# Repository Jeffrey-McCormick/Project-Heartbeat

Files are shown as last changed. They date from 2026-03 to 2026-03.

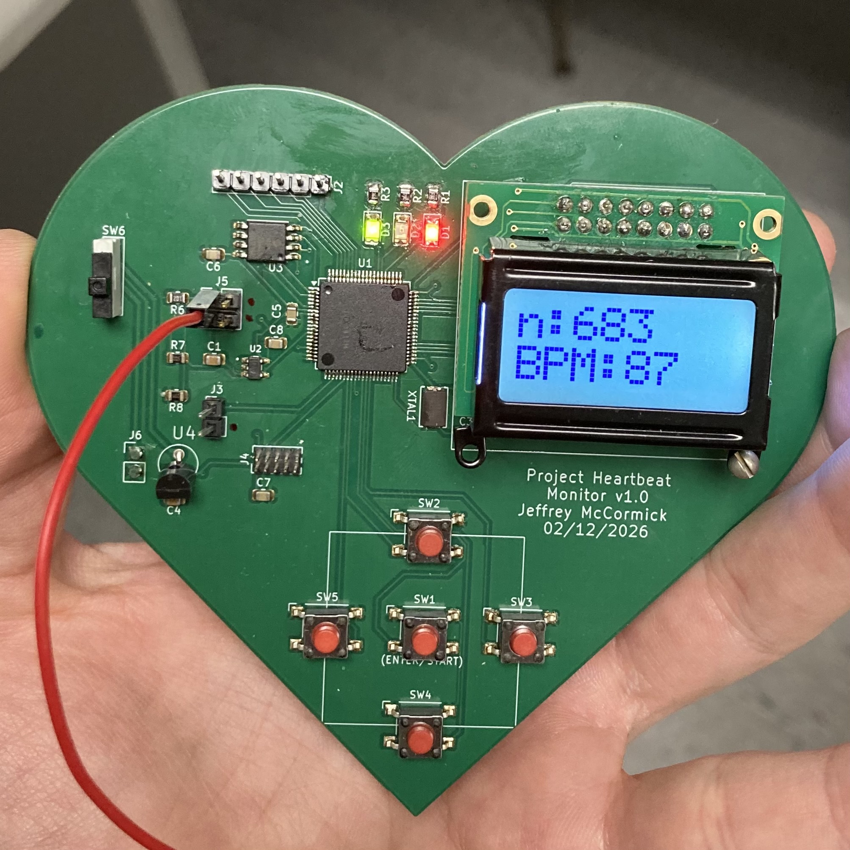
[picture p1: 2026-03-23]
IMG_8756.jpeg

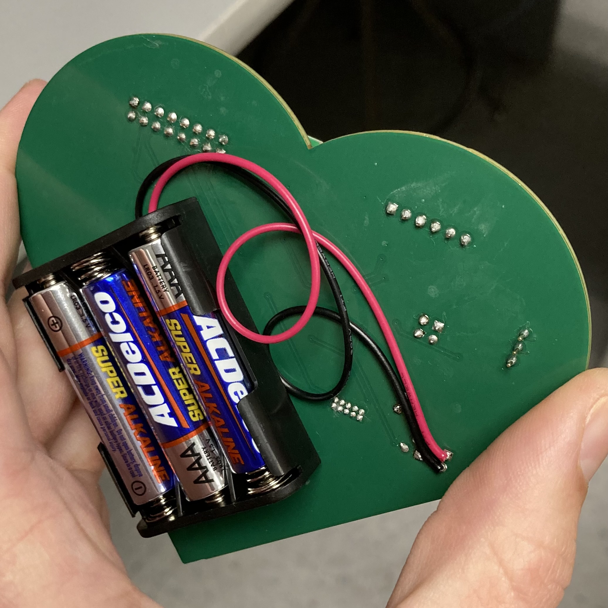
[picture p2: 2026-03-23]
IMG_8758.jpeg

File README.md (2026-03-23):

Hello! Welcome to Project Heartbeat, my individual project for my ENGR 355 - Embedded System Design class.
This project's first revision is finished and turned in for credit. Later versions may appear as I have opportunity to expand this heartrate monitor's capabilities. I used KiCad and ARM Keil applications for designing and programming the board. 

I encourage you to read the Project Heartbeat Design Report to understand my design approach as well as what the functions of my code are for. 
Although, you should be able to read the comments in my code and understand what is happening. 

Here is what it looked like in KiCad and in reality.




The text I used was produced by ARM Education. Here is the Github resource: https://github.com/arm-education/Embedded-Systems-Fundamentals?tab=readme-ov-file

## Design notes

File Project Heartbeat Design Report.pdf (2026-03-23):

# Project Heartbeat’s Embedded System Design

Jeffrey A. McCormick, Student, Walla Walla University

Abstract— This project seeks to use an analog to digital converter (ADC) to determine the heartrate of a person from an analog electrocardiogram (EKG) waveform.

I. INTRODUCTION
IGNAL processing is at the foundation of many breakthrough technologies. From car radios to medical scanning systems, most of all sensor equipment is used to measure continuous “real-world analog signals”. [3] By using an ADC, those analog signals can then be processed digitally on, say, a computer or calculator or an FPGA.
For the embedded system called Project Heartbeat, an ADC will be used to convert an analog heartbeat signal and use the digital representation of it to compute and display for the user an extrapolated beats per minute (BPM) measure.

II. DESIGN METHODS: HARDWARE
The general approach to designing the hardware for Project Heartbeat relied heavily on the KL25Z FRDM board,ENGR 355 Dev board, and LCD specifications. Since their designs worked well together, making a custom Printed Circuit Board (PCB) that would seamlessly integrate into this system was paramount. A distinct benefit of using this approach was that I could program and test using the Dev board, while the parts and custom PCB were being delivered.
While the Dev board schematic was the pattern, there were several changes of note. First, the system had to be portable, meaning that the Project Heartbeat device would have to be battery powered. To accommodate this, a physical on-off switch and a voltage regulator were added to the schematic. The supplied voltage from the regulator was 3.3V to be used as power for the rest of the system.
Second, | in | order | to | program | the | MKL25Z128
microcontroller (MCU), a 10-pin header Serial Wire Debug (SWD) interface was added. The FRDM board would connect to this interface but only use six of the ten pins. Per the FRDM KL25Z Schematic indicating that the SWD clock and digital input/output pins should go on Port A pins 0 and 3, respectively, some of the switches were displaced to other pins.
Third, the five switches were still connected to Port A of the MCU so that they could have interrupt capabilities, but they were rearranged. The layout of the PCB was to have the five buttons arranged like a Swiss cross with SW1 centered and the others ordered sequentially clockwise around it. By this schematic arrangement, their traces on the PCB were more organized, taking up less space and reducing the risk of layout

mistakes.
Fourth, six GPIO pins were placed on Port D, because that gives the designer maximum future project flexibility in case they wish to use interrupts with such pins.
Fifth, an EEPROM memory chip was added. Again, this was chosen with future projects by the designer in mind, providing a way for users to read and write data for long-term storage without burdening the microcontroller’s memory. Sixth, the ADC input was designed for both DC and AC coupling. The AC coupling input passes through a voltage divider such that a signal of 0V AC enters the buffering source follower op amp, delivering an input of 1.65 V into the ADC. DC inputs are simply buffered without the scale shift.
As good practice, coupling capacitors were placed near the power pins of the MCU, SWD interface, LCD interface, ADC source follower op amp, and EEPROM. These were chosen to dampen any voltage fluctuations in the 3.3V power and to reduce the risk of noise adding to the signals.
The PCB layout was designed for an easy and intuitive user experience as well as convenient debugging and flexible application. Many people in this modern digital era are familiar with Gameboy or other handheld Nintendo products, so the Project Heartbeat board layout was modeled after them. The hope is that a user can figure out how to use the board by drawing on this familiarity of an LCD screen with buttons below it. Since the primary use case of the board was to detect and calculate heartbeat behavior, it seemed fitting to let the user’s intuition know that by making the board heart shaped. Although it may still be encased within a plastic covering, the board could still be used pleasantly without the covering by designers, developers, and debuggers. Therefore, the size of the board was made approximately 4 inches by 3 inches to fit comfortably in an average person’s hand(s), even though a more compact layout could have had the same electronic functionality. With a less compact layout, the board’s components can be easily accessed by a developer trying to debug the circuitry.

S

IMAGE 1
THIS IS THE FRONT VIEW

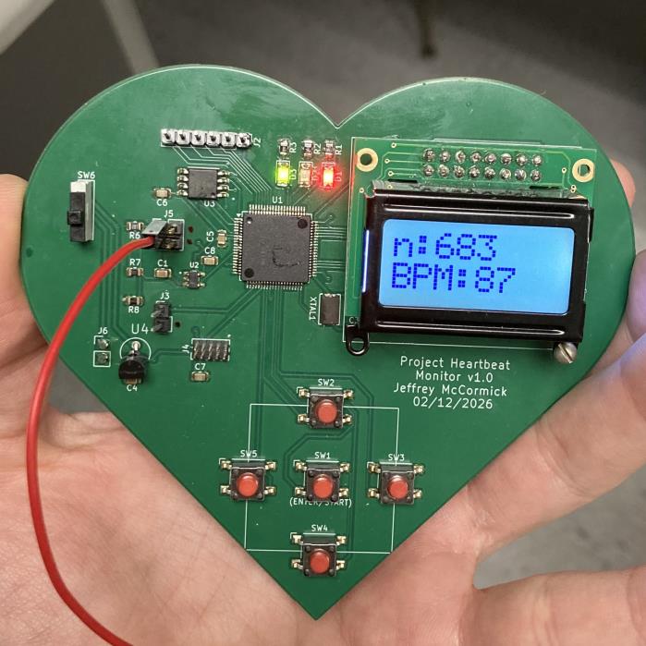
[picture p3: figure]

McCor1.jpeg

IMAGE 1
THIS IS THE BACK VIEW

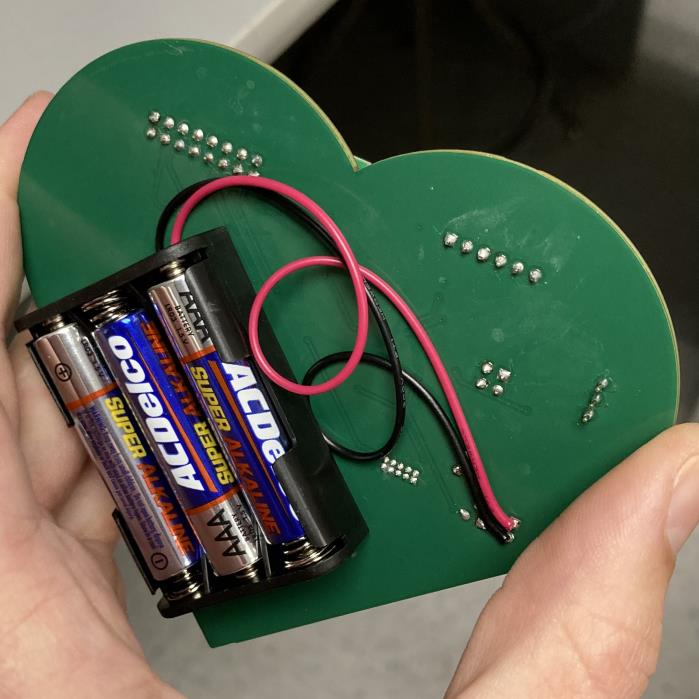
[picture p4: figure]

McCor2.jpeg

IV. DESIGN METHODS: SOFTWARE The software of Project Heartbeat was made for the primary use case of receiving a continuous analog heartbeat signal and output the BPM corresponding to the interval between the last two beats sensed. To make debugging easier, a modular approach was taken. The “main” function served as the testbench code for each function as they were being developed. This strategy ensured that any errors in the inputs and outputs of a function were caught early and corrected. Artificial intelligence (AI) was used as a tool to expedite each function’s code generation by prompting with specific desired inputs, outputs, purpose, and role in the software and project as a whole. Because the software functions are not placed in order of their dependency in the “Lab_8_Code.c” c-language code file, the following explanations of the code will be presented in order of their dependency from input to output.

A. Enable the Clocks
This ENABLE_CLKS() function enables the default system clock signal in Clock Setup 1 (48MHz) to go to Ports A, B, C, and E of the MCU. It is mostly just to ensure the code is completely enabled or disabled by whether the function is called or not, respectively.
B. Initialize ADC
The Init_ADC() function sets the ADC to:
1) 12-bit conversion standard
2) Clock division by 4
3) Clock source of ADICLK (default)
It also enables the ADC0 conversion complete flag (COCO) to trigger an interrupt to be handled in the ADC IRQ Handler.
C. Initialize SysTick Interrupts
For use in other functions as an independent timer from the PIT, this Init_SysTick() function simply sets the ticks to occur once every 1ms and trigger an interrupt with it.
D. Initialize PIT and Define Its IRQ Handler
Similar to the SysTick initialization, the PIT_init() function serves to enable interrupts which occur exactly once per 1ms. It’s PIT_IRQHandler() function can then increment the two counters used by the buttons for debouncing and the heartbeat interval calculator for measurement. A green LED is linked to every PIT flag raising so that the user can know if the device is on and running.
E. Initialize Buttons and Define Their Port A ISR Handler Init_Buttons() sets all the buttons to input GPIOs with pull-up resistor setting configured in the MCU and with interrupt capabilities. Then, because the buttons are on Port A, the PORTA_IRQHandler() function triggers when a button is pressed and uses the system millisecond counts from the PIT to debounce the button press and set a program flag as true.

F. Initialize the DAC
This Init_DAC() function simply sets the DAC as active and referencing the same reference voltage as the other components.
G. Define ADC IRQ Handler
This ADC0_IRQHandler() function operates in two modes. Mode 1 is the most useful mode, because it sets the DAC to be an output for reconstruction of the input heartbeat signal. Mode 2 sets the DAC as a simulator essentially so it does not need to be tied to the ADC’s output.
The function triggers whenever the input converted signal crosses the threshold and hysteresis digital voltage values. They can be set to DC and AC coupling, which only changes whether the interrupt is triggered on the rising or falling edge of a beat. See code comments for examples.
A red LED is used as an indicator that a conversion happened.
H. Get the Heartbeat from the ADC Signal
When a conversion completes, this get_heartbeat() function simply captures the current PIT count in the interval between beats and resets the count to be ready for the next beat. The PIT increments every 1ms, so the PIT counts that happened in the interval is equivalent to the number of milliseconds between the beats.
I. Initialize LEDs
This Init_LEDs() function simply sets the LEDs to GPIO outputs so that they can be used as indicator lights.
J. Get BPM from the Heartbeat Intervals in Milliseconds This get_bpm() function is the convert the beat interval in ms found by the get_heartbeat() function into the calculated BPM corresponding to a period equal to the length of that interval. While this lends itself to greater fluctuation in the calculated BPM for small deviations from an average input signal’s BPM, it allows for processing as close to present as possible so that a “live” data stream can be viewed by the user. The calculation uses integer math to save computation time and memory space of the MCU. Again, the goal is as close to a real-time update as possible.
K. Initialize LCD and Display a String of Relevant Data Using the unaltered “lcd_lib_4bit_20b.c” LCD library of commands file written by Dr. Larry Aamodt, the LCD_init() function initializes the LCD. Displaying a string on any selectable line of the LCD is the purpose of the displayString() function. By supplying a character array to display and the line selection of 0 for the top line and 1 for the bottom line, the LCD will display only the first 8 characters in the string on the selected line. This function allows explicit developer control over what is shown on the LCD screen.
L. The Main Function
The main function calls all of the above functions as needed for scope or simulator modes of the device. Within a while loop running faster than the 1ms PIT or SysTick interrupts, get_heartbeat() checks for a beat from the ADC, a simple LCD user interface tells users what the state of the program is, and running logic critical for “live” updates of the LCD ensures that recently captured and processed signal data is displayed on the LCD without race conditions. With the large amount of interrupts and the random nature of when a signal could enter the ADC, it is important that the transmission to the LCD finish before seeking another one. This could potentially cause under counting, but not if the signal period is greater than 2ms, which is true for heartbeat signals even up into the arithmetic heart rates (500+ BPM). Another timing aspect of the running logic is that the LCD should only update the display when the measured period between the beats actually changes. This task reduction results in more stable display behavior.
V. RESULTS

A demonstration of the Project Heartbeat board working as a live heartrate monitor in action was performed on March 17, 2026 on Jeffrey McCormick. Medical-grade EKG pads were placed at each shoulder and his left leg. The leads connected to an isolated amplifier circuit board made by Dr. Larry Aamodt, which then sent the signal ranging from 0v to 3.3V to the ADC input pins on the Project Heartbeat board.
The initial result was very high BPM measurements. To see what thresholds to adjust the code to, an oscilloscope was connected to the Project Heartbeat ADC pins. After increasing the threshold, the board read the live heartbeat signals within 5 percent error of the value from a standard Oura Ring 4
simultaneously | measuring | the | live | heart | rate | from
McCormick’s index finger.

VI. CONCLUSION

Overall, Project Heartbeat as a physical, custom embedded system met its essential requirements as specified by instructor Dr. Natalie Smith-Gray. It is “a hand-held portable instrument that can analyze a periodic analog input signal (voltage)[1] While its embedded system demonstrates promise, it can still be improved by adding a filtering or stream-averaging scheme to the software, more functions like HRV measurements, and a visually and physically appealing plastic case to hold it.

REFERENCES

[2] N. Smith-Gray, “ENGR 355 Course Project,”unpublished. Winter 2026. https://class.wallawalla.edu/d2l/le/lessons/379831/topics/4176668
[3] Nintendo Co. Game Boy. https://nintendo.fandom.com/wiki/Game_Boy (Accessed 18 Mar 2026)
[4] IC Online, “ADC vs DAC Key Differences and Modern Electronics
Applications,” | https://ic-online.com/blog/post/adc-vs-dac-key-
differences-and-modern-electronics-applications(Accessed 18 Mar 2026)

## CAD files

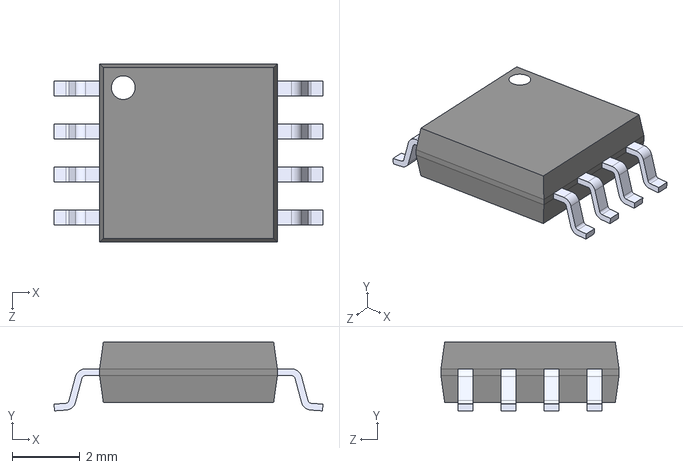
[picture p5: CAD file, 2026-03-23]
Project Heartbeat KiCad/P_4.1_2026_Jeff_M/25LC1024_I_SM/25LC1024-I_SM.step
7.94 x 2.03 x 5.26 mm

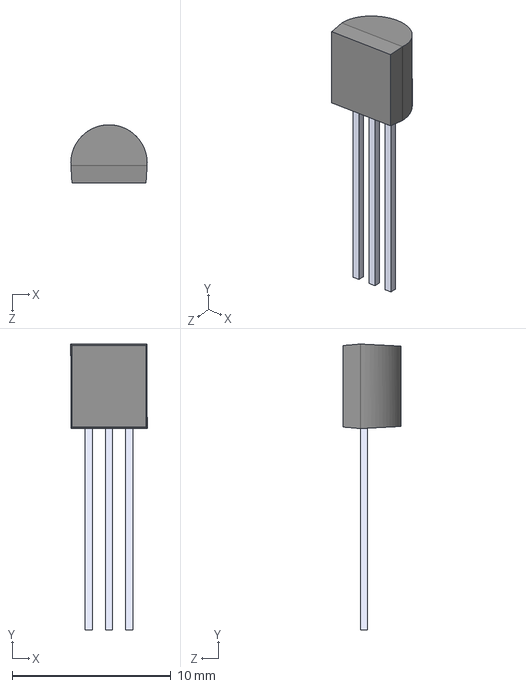
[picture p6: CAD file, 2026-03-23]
Project Heartbeat KiCad/P_4.1_2026_Jeff_M/MCP1700_3302E_TO/MCP1700-3302E_TO.step
4.82 x 18.0 x 3.68 mm

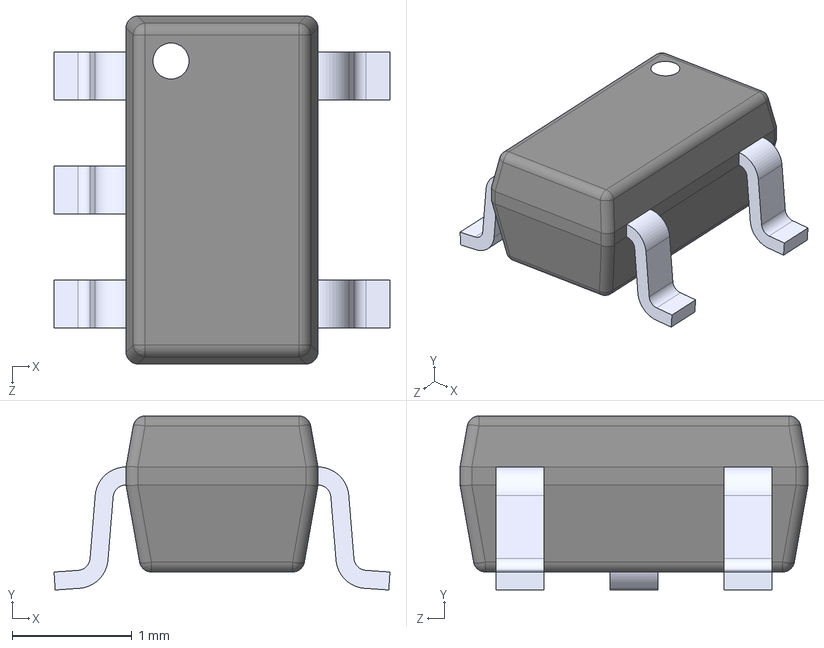
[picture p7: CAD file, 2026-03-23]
Project Heartbeat KiCad/P_4.1_2026_Jeff_M/OPA377AIDBVR/OPA377AIDBVR.step
2.80 x 1.45 x 2.90 mm

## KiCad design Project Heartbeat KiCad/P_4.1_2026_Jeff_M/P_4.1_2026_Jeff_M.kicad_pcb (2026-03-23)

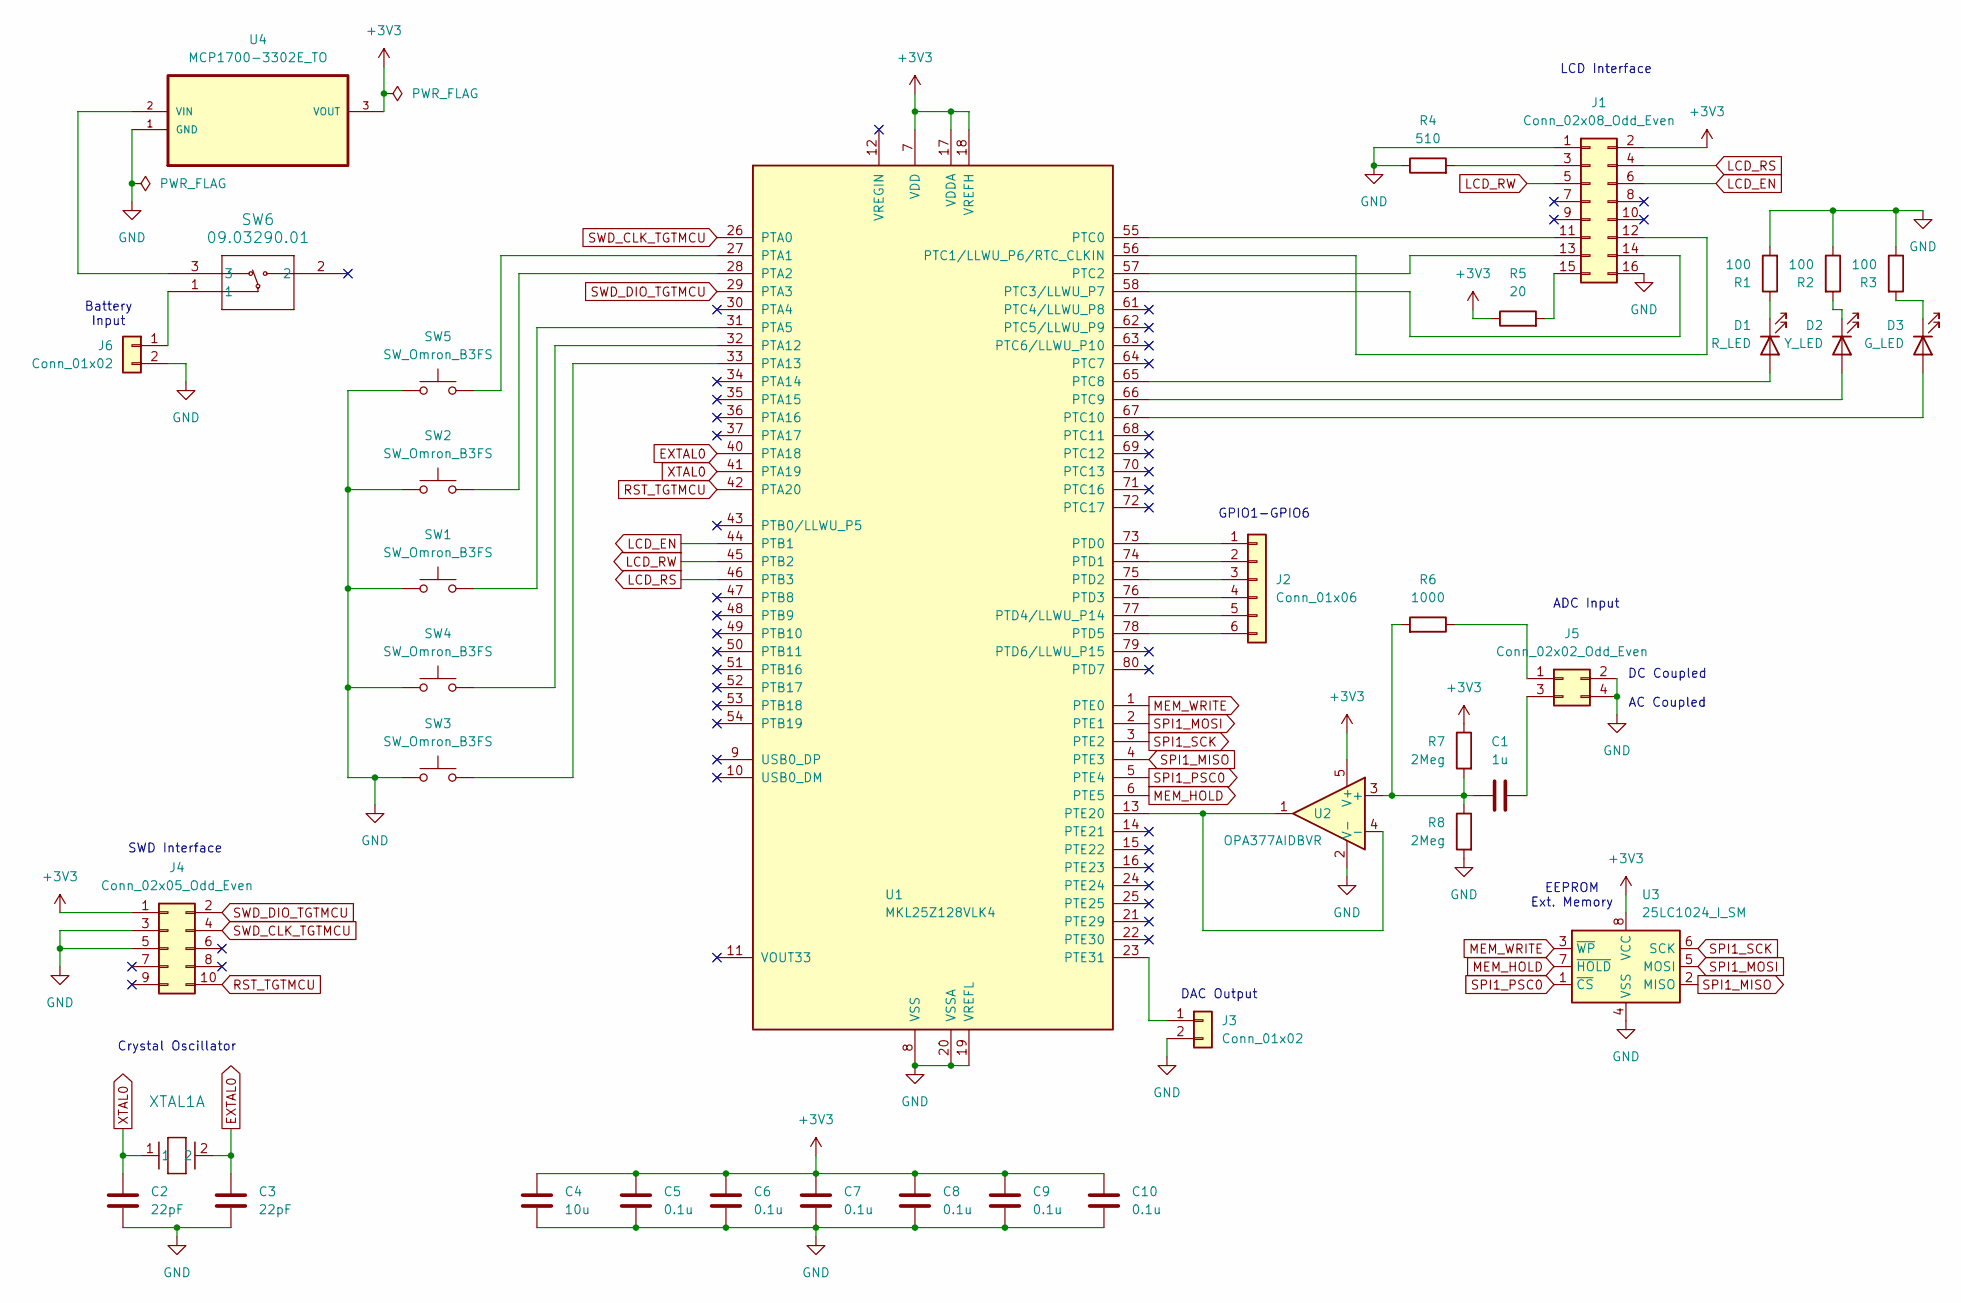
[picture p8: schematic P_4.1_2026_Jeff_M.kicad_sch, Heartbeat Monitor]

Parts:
C1: 1u; C_0805_2012Metric
C2, C3: 22pF; C_0805_2012Metric
C4: 10u; C_0805_2012Metric
C5, C6, C7, C8, C9, C10: 0.1u; C_0805_2012Metric
D1: R_LED; LED_1206_3216Metric
D2: Y_LED; LED_1206_3216Metric
D3: G_LED; LED_1206_3216Metric
J1: Conn_02x08_Odd_Even; PinHeader_2x08_P2.54mm_Vertical
J2: Conn_01x06; PinHeader_1x06_P2.54mm_Vertical
J3, J6: Conn_01x02; PinHeader_1x02_P2.54mm_Vertical
J4: Conn_02x05_Odd_Even; PinHeader_2x05_P1.27mm_Vertical
J5: Conn_02x02_Odd_Even; PinHeader_2x02_P2.54mm_Vertical
R1, R2, R3: 100; R_0805_2012Metric
R4: 510; R_0805_2012Metric
R5: 20; R_0805_2012Metric
R6: 1000; R_0805_2012Metric
R7, R8: 2Meg; R_0805_2012Metric
SW1, SW2, SW3, SW4, SW5: SW_Omron_B3FS; SW_SPST_Omron_B3FS-101xP
SW6: 09.03290.01; 09.03290_EAO
U1: MKL25Z128VLK4; LQFP-80_12x12mm_P0.5mm
U2: OPA377AIDBVR; SOT95P280X145-5N
U3: 25LC1024_I_SM; SOIC127P794X202-8N
U4: MCP1700-3302E_TO; TO127P254X495-3; MPN MCP1700-3302E/TO
XTAL1: ABM3-8.000MHZ-D2Y-T; XTAL_ABM3-8.000MHZ-D2Y-T_ABR

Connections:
+3V3: C4.1, C5.1, C6.1, C7.1, C8.1, C9.1, C10.1, J1.2, J4.1, R5.1, R7.1, U1.7 (VDD), U1.17 (VDDA), U1.18 (VREFH), U1.38 (VDD), U1.60 (VDD), U2.5 (V+), U3.8 (VCC), U4.3 (VOUT)
EXTAL0: C3.1, U1.40 (PTA18), XTAL1.2
GND: C2.2, C3.2, C4.2, C5.2, C6.2, C7.2, C8.2, C9.2, C10.2, J1.1, J1.16, J3.2, J4.3, J4.5, J5.2, J5.4, J6.2, R1.2, R2.1, R3.1, R4.1, R8.2, SW1.1, SW2.1, SW3.1, SW4.1, SW5.1, U1.8 (VSS), U1.19 (VREFL), U1.20 (VSSA), U1.39 (VSS), U1.59 (VSS), U2.2 (V-), U3.4 (VSS), U4.1 (GND)
LCD_EN: J1.6, U1.44 (PTB1)
LCD_RS: J1.4, U1.46 (PTB3)
LCD_RW: J1.5, U1.45 (PTB2)
MEM_HOLD: U1.6 (PTE5), U3.7 (~HOLD)
MEM_WRITE: U1.1 (PTE0), U3.3 (~WP)
unnamed: D1.2 (A), U1.65 (PTC8)
unnamed: D1.1 (K), R1.1
unnamed: D2.2 (A), U1.66 (PTC9)
unnamed: D2.1 (K), R2.2
unnamed: D3.2 (A), U1.67 (PTC10)
unnamed: D3.1 (K), R3.2
unnamed: J1.3, R4.2
unnamed: J1.11, U1.55 (PTC0)
unnamed: J1.12, U1.56 (PTC1/LLWU_P6/RTC_CLKIN)
unnamed: J1.13, U1.57 (PTC2)
unnamed: J1.14, U1.58 (PTC3/LLWU_P7)
unnamed: J1.15, R5.2
unnamed: J2.1, U1.73 (PTD0)
unnamed: J2.2, U1.74 (PTD1)
unnamed: J2.3, U1.75 (PTD2)
unnamed: J2.4, U1.76 (PTD3)
unnamed: J2.5, U1.77 (PTD4/LLWU_P14)
unnamed: J2.6, U1.78 (PTD5)
unnamed: J3.1, U1.23 (PTE31)
unnamed: J5.1, R6.1
unnamed: C1.1, J5.3
unnamed: J6.1, SW6.1
unnamed: SW5.2, U1.27 (PTA1)
unnamed: SW2.2, U1.28 (PTA2)
unnamed: SW1.2, U1.31 (PTA5)
unnamed: SW4.2, U1.32 (PTA12)
unnamed: SW3.2, U1.33 (PTA13)
unnamed: U1.13 (PTE20), U2.1, U2.4 (-)
unnamed: C1.2, R6.2, R7.2, R8.1, U2.3 (+)
unnamed: SW6.3, U4.2 (VIN)
RST_TGTMCU: J4.10, U1.42 (PTA20)
SPI1_MISO: U1.4 (PTE3), U3.2 (MISO)
SPI1_MOSI: U1.2 (PTE1), U3.5 (MOSI)
SPI1_PSC0: U1.5 (PTE4), U3.1 (~CS)
SPI1_SCK: U1.3 (PTE2), U3.6 (SCK)
SWD_CLK_TGTMCU: J4.4, U1.26 (PTA0)
SWD_DIO_TGTMCU: J4.2, U1.29 (PTA3)
XTAL0: C2.1, U1.41 (PTA19), XTAL1.1

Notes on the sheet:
DAC Output
GPIO1-GPIO6
SWD Interface
Crystal Oscillator
Battery Input
EEPROM Ext. Memory
LCD Interface
ADC Input
DC Coupled AC Coupled

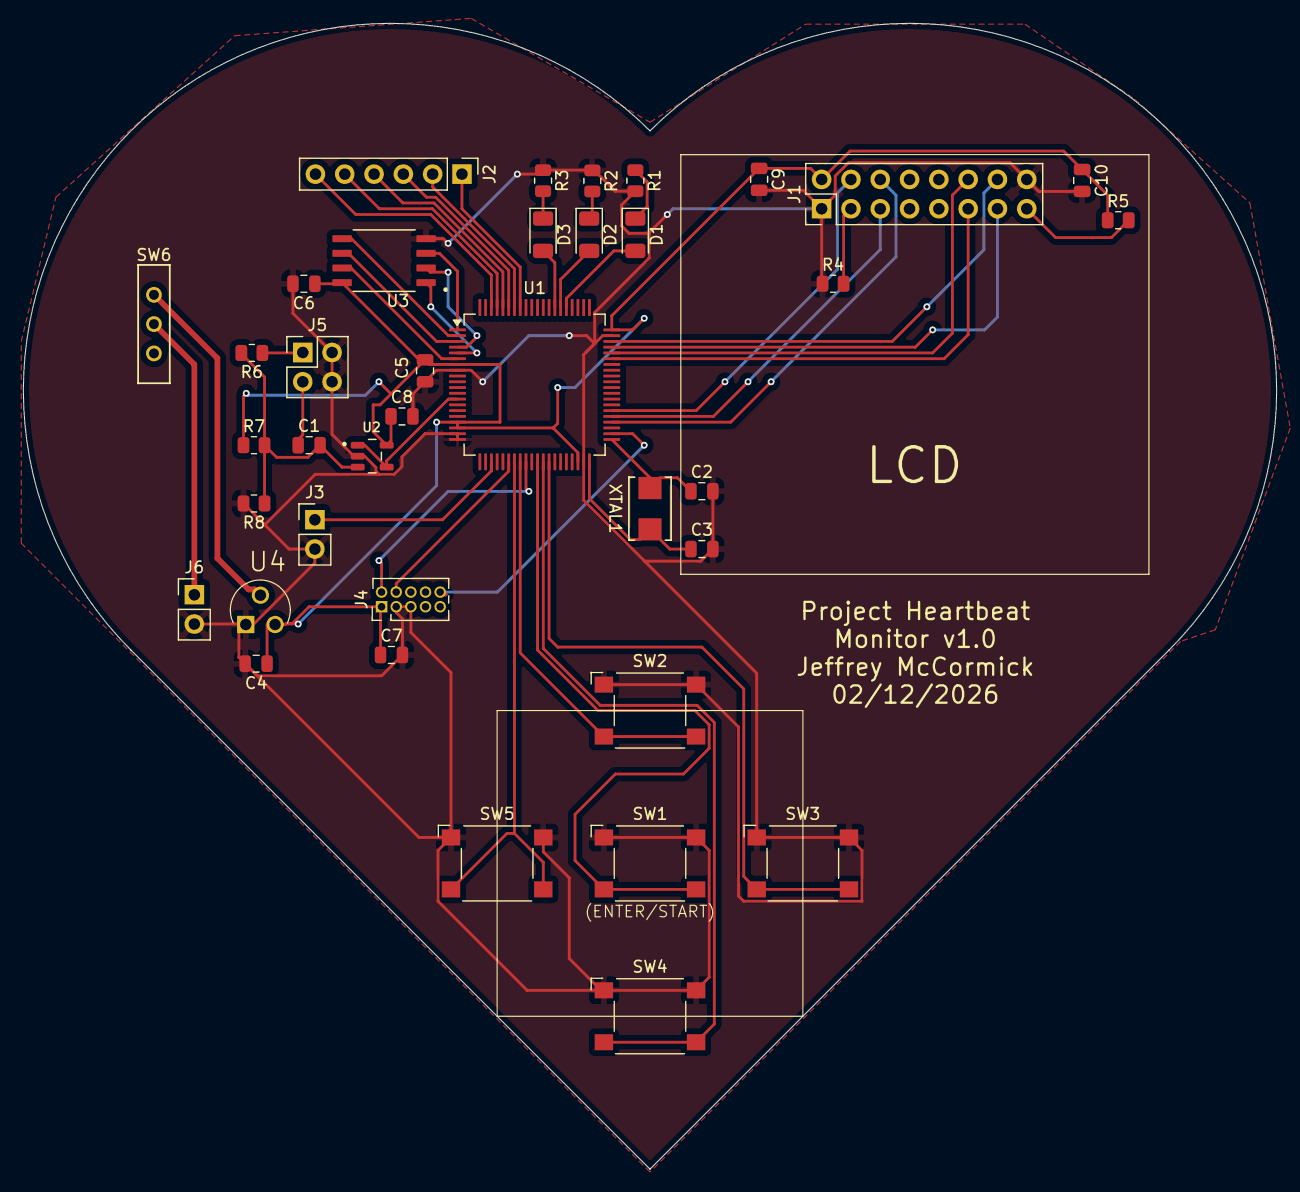
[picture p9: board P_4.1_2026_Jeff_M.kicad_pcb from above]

Board: 2 copper layers, 108.6 x 99.3 mm, 38 parts (0 on the bottom side), 46 nets.

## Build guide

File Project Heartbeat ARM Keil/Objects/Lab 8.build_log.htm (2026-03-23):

µVision Build Log

Tool Versions:

IDE-Version: µVision V5.43.1.0
Copyright (C) 2025 ARM Ltd and ARM Germany GmbH. All rights reserved.
License Information: S L, Walla Walla University, LIC=----
 
Tool Versions:
Toolchain:       MDK-Lite  Version: 5.43.0.0
Toolchain Path:  C:\Program Files\Keil\MDK-Arm\ARM\ARMCLANG\Bin
C Compiler:      ArmClang.exe V6.24
Assembler:       Armasm.exe V6.24
Linker/Locator:  ArmLink.exe V6.24
Library Manager: ArmAr.exe V6.24
Hex Converter:   FromElf.exe V6.24
CPU DLL:         SARMCM3.DLL V5.43.0.0
Dialog DLL:      DARMCM1.DLL V1.19.6.0
Target DLL:      CMSIS_AGDI.dll V1.33.24.0
Dialog DLL:      TARMCM1.DLL V1.14.6.0

Project:

K:\STEM\Student\Jeffrey McCormick (2063479)\Winter 26\Embedded_Systems\Lab 8\Lab 8.uvprojx
Project File Date:  03/15/2026

Output:

*** Using Compiler 'V6.24', folder: 'C:\Program Files\Keil\MDK-Arm\ARM\ARMCLANG\Bin'
Build target 'Target_1'
compiling Lab_8_Code.c...
linking...
Program Size: Code=10096 RO-data=828 RW-data=24 ZI-data=424  
".\Objects\Lab 8.axf" - 0 Error(s), 0 Warning(s).

Software Packages used:

Package Vendor: ARM
                https://www.keil.com/pack/ARM.CMSIS.6.2.0.pack
                ARM::CMSIS@6.2.0
                CMSIS (Common Microcontroller Software Interface Standard)
   * Component: CORE Version: 6.1.1

Package Vendor: Keil
                https://www.keil.com/pack/Keil.Kinetis_KLxx_DFP.1.15.1.pack
                Keil::Kinetis_KLxx_DFP@1.15.1
                NXP Kinetis KLxx Series Device Support and Examples
   * Component: Startup Version: 2.5.0

Collection of Component include folders:

  ./RTE/Device/MKL25Z128xxx4
  ./RTE/_Target_1
  C:/Program Files/Keil/MDK-Arm/Packs/ARM/CMSIS/6.2.0/CMSIS/Core/Include
  C:/Program Files/Keil/MDK-Arm/Packs/Keil/Kinetis_KLxx_DFP/1.15.1/Device/Include

Collection of Component Files used:

   * Component: ARM::CMSIS:CORE@6.1.1

   * Component: Keil::Device:Startup@2.5.0
      Source file:   Device/Source/system_MKL25Z4.c
      Include file:  Device/Source/system_MKL25Z4.h
      Source file:   Device/Source/ARM/startup_MKL25Z4.s
Build Time Elapsed:  00:00:02

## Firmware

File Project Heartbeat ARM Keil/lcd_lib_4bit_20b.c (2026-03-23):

/*----------------------------------------------------------------------------*/
/*  LCD initialization and data transfer routines                             */
/*       4-bit bus version                                                    */
/*  Filename: lcd_lib_4bit_20b.c                                              */
/*  Author:   Larry Aamodt                                                    */
/*  Version:  1/25/19 written                                                 */
/*            1/28/19 updated                                                 */
/*            1/29/20 updated for wtr 2020 project                            */
/*            2/12/20 revised LCD control signal port & pins                  */
/*            3/10/21 added defines for cursor commands                       */
/*            1/19/22 updated comments re clock turn on. No code changes      */
/*  Compiler: Keil uVision5                                                   */
/*  Hardware: NXP Freedom board & a 2x8 or 2x16 LCD display w/parallel interfc*/
/*            PORT B  bits 1,2,3 used for control                             */
/*            PORT C  bits 0,1,2,3 used for data                              */
/*  Software note:  A software loop is used for time delay generation         */
/*        Port B and C clocks must be turned on before calling these routines */
/*  Function use:   call LCD_command to move the cursor, clear screen, etc.   */
/*                  call LCD_send_data to send one ASCII character code       */
/*----------------------------------------------------------------------------*/
#include <stdint.h>
#include <MKL25Z4.h>

#define LCD_EN              0x00000002    // PTB1 LCD enable 
#define LCD_RW              0x00000004    // PTB2 LCD read/write
#define LCD_RS              0x00000008    // PTB3 LCD RS
#define LCD_LOW4_MASK       0x0000000F    // low 4 bits of a command
#define LCD_UPPER4_MASK     0x000000F0    // upper 4 bits of a command
#define LCD_MASK            0x0000000F    // PortC bits 0-3
#define LCD_DATA_PINS       0x0000000F    // PortC LCD data pins
#define LCD_CNTRL_PINS      0x0000000E    // PortB LCD control pins

#define clear_screen 0x01
#define cursor_left 0x10
#define cursor_right 0x14
#define cursor_line1 0x80
#define cursor_line2 0xC0


/*----------------------------------------------------------------------------
  LCD functions 
 *----------------------------------------------------------------------------*/
void LCD_command(uint32_t command);       // use to send LCD commands
void LCD_send_data(uint32_t data);        // use to send one char to screen
void delayMs(uint32_t n);
void pulse_the_LCD_enable(void);
void LCD_init(void);

/*----------------------------------------------------------------------------
  Initialize the LCD in 4-bit bus mode.         L.Aamodt
 *----------------------------------------------------------------------------*/
void LCD_init(void)
{
  // Note: you need to turn on Port B and C clocks prior to calling this routine

	uint32_t k;

     // First set up bits in GPIO Port C used by the LCD
	for (k=0; k<4; k++) {                  // make ports GPIO
	PORTC->PCR[k] &= ~PORT_PCR_MUX_MASK;    // 4 LCD data bits
	PORTC->PCR[k] |= PORT_PCR_MUX(1);
	}
	
	for (k=1; k<4; k++) {                   // make ports GPIO
	PORTB->PCR[k] &= ~PORT_PCR_MUX_MASK;    //   LCD control 3-bits 
	PORTB->PCR[k] |= PORT_PCR_MUX(1);	
	}
	
	PTC->PDDR |= LCD_DATA_PINS;             // set ports to output
	PTB->PDDR |= LCD_CNTRL_PINS;

	PTB->PCOR = LCD_RW | LCD_RS | LCD_EN;   // clear R/W, RS, and EN	
		// Now initialize the LCD itself
	delayMs(00);
	PTC->PCOR = LCD_MASK;                   // clear output data bits to 0
	PTC->PSOR = (0x3);                   // put a wake-up value on bus
	delayMs(10);
	pulse_the_LCD_enable();
	delayMs(1);
	pulse_the_LCD_enable();
	delayMs(1);
	pulse_the_LCD_enable();
	delayMs(1);
	PTC->PCOR = LCD_MASK;                   // clear output data bits to 0
	PTC->PSOR = (0x2);                   // initialize to 4-bit bus mode
	delayMs(10);
	pulse_the_LCD_enable();
	LCD_command(0x28);                      // Set to 4-bit/2-line/5x7pixels
	LCD_command(0x10);                      // 
	LCD_command(0x0F);                      // Display on, cursor on and blink
	LCD_command(0x06);                      //
}
/*----------------------------------------------------------------------------
  Send a command to the LCD                      L.Aamodt
 *----------------------------------------------------------------------------*/
void LCD_command(uint32_t command)
{
	PTB->PCOR = LCD_RW | LCD_RS | LCD_EN;   // clear R/W, RS, and EN
	PTC->PCOR = LCD_MASK;                   // clear output data bits to 0
	PTC->PSOR = (command & LCD_UPPER4_MASK)>>4; // output upper 4 bits of command
	pulse_the_LCD_enable();
	PTC->PCOR = LCD_MASK;                   // clear output data bits
	PTC->PSOR = (command & LCD_LOW4_MASK);   // output lower 4 bits
	pulse_the_LCD_enable();
	if (command < 4)
		delayMs(3);                           // command 1 and 2 need 1.64ms
	else
		delayMs(1);                           // all others 40us
}
/*----------------------------------------------------------------------------
   Pulse the LCD enable line                    L.Aamodt
 *----------------------------------------------------------------------------*/
void pulse_the_LCD_enable(void)
{
	PTB->PSOR = LCD_EN;                     // assert enable
	delayMs(1);
	PTB->PCOR = LCD_EN;                     // de-assert enable
}

/*----------------------------------------------------------------------------
   Send data (one character, using ASCII code) to the LCD      L.Aamodt
 *----------------------------------------------------------------------------*/
void LCD_send_data(uint32_t data)
{
	PTB->PCOR = LCD_RW | LCD_EN;            // clear R/W, RS, and EN
	PTB->PSOR = LCD_RS;                     // set RS high
	PTC->PCOR = LCD_MASK;                   // clear output data bits to 0
	PTC->PSOR = (data & LCD_UPPER4_MASK)>>4;   // output upper 4 bits of command
	pulse_the_LCD_enable();
	PTC->PCOR = LCD_MASK;                   // clear output data bits
	PTC->PSOR = (data & LCD_LOW4_MASK);  // output lower 4 bits
	pulse_the_LCD_enable();
}
/*----------------------------------------------------------------------------
  Delay, used with the LCD routines.  Delay specified in units of milliseconds
      The inner loop max count should be 3500 for 20.97 MHZ system clock rate
      or 8000 for 48 MHZ system clock rate                      L.Aamodt
 *----------------------------------------------------------------------------*/
void delayMs(uint32_t n)
{
uint32_t i;
uint32_t j;
for(i=0; i < n; i++)
		for(j=0; j < 3500; j++) {}
}

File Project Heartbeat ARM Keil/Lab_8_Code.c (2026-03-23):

// Lab 8 - Analog Heartbeat Measurement 
//
//Written by Jeffrey McCormick
// With assistance from Dr. Larry Aamodt, Dr. Natalie Smith-Gray,
// Peter Kyle, and Google Gemini 2.5


#include <MKL25Z4.h>
#include <string.h>
#include <stdio.h>

#define CLOCK_SETUP 1		// 48MHz DEFAULT_SYSTEM_CLOCK
#define MASK(x) (1UL << (x))

#define ADC_POS		(20)	// PTE20
#define DAC_POS		(31)	// PTE31 and 30 on ENGR355 Dev board

#define R_LED (8)
#define Y_LED (9)
#define G_LED (10)		//Port-C Pin 10

// Button Pin Definitions
#define SW1 (5)   // PTA5
#define SW2 (2)   // PTA2
#define SW3 (13)  // PTA13
#define SW4 (12)  // PTA12
#define SW5 (1)   // PTA1

// Global Variables
int DAC_RES= 1<<12; 									// 12-bit DAC 2^12 values
// Mode 0: Simulation (DAC generates pulse for loopback logic testing)
// Mode 1: Scope (DAC reconstructs ADC input for oscilloscope viewing and hardware testing)
volatile int dac_mode = 1;
volatile uint32_t n_counts = 0;				// Note: Freq_pit = 1000 and counts >59999 --> BPM = 0 (beat period is greater than 1 min.)
float Freq_pit = 1000;								//Hz
																			// T_pit = 1/Freq_pit -> Multiplication reduces computation time.
float T_pit = 0.001;									//sec	Effectively the sampling resolution
volatile uint32_t pit_count = 0; 			// Incremented by ISR
volatile uint32_t system_ms = 0; 			// Always increments, never resets
volatile int beat_trig = 0;						// 0=False, 1=True Link to button/sim for Debug
volatile int waiting_for_first_beat = 1;		// Tracks state in HB_program's get_heartbeat()
volatile int program_start = 0;				// 0=False, 1=True Linked to button
char line0[16]; 
char line1[16];
uint32_t last_n = 0;
int last_start_state = -1; 						// Track if the user just toggled the button
// Selectable program flags (Only set one at a time)
int HB_prog = 1;
int program2 = 0;
int program3 = 0;


	
// Prototypes
void Init_DAC(void);
void DAC_Scope(uint16_t adc_value);
void Init_SysTick(void);
void Init_ADC(void);
void Init_Buttons(void);
void Init_LEDs(void);
void LCD_init(void);
void LCD_command(uint32_t command);       // use to send LCD commands
void LCD_send_data(uint32_t data);        // use to send one char to screen
void delayMs(uint32_t n);
void get_heartbeat(void);

void ENABLE_CLKS(void) {
	
	// Enable clock to Ports A, B, C, and E
	SIM->SCGC5 |= SIM_SCGC5_PORTA_MASK;
	SIM->SCGC5 |= SIM_SCGC5_PORTB_MASK;
	SIM->SCGC5 |= SIM_SCGC5_PORTC_MASK;
	SIM->SCGC5 |= SIM_SCGC5_PORTE_MASK;
	}
void Init_SysTick(void) {			// For Heartbeat Simulator
    // SystemCoreClock is 48 MHz when CLOCK_SETUP == 1
    // We want a 10 kHz sample rate (10,000 interrupts per second)
    // 48,000,000 / 10,000 = 4,800 ticks between interrupts
    SysTick_Config(SystemCoreClock / 1000);
		NVIC_SetPriority(SysTick_IRQn, 3); // Lower priority than PIT (2)
}
void Init_Buttons(void) {
    // Enable clock to Port A if no otherwise enabled
    //SIM->SCGC5 |= SIM_SCGC5_PORTA_MASK;

    // 1. Configure SW1 for: GPIO + Pull-up + Falling Edge Interrupt (0xA)
    PORTA->PCR[SW1] = PORT_PCR_MUX(1) | PORT_PCR_PE_MASK | PORT_PCR_PS_MASK | PORT_PCR_IRQC(0x0A);
    
    // 2. Configure other buttons as normal GPIO + Pull-up (no interrupts for now)
    uint32_t other_btn_cfg = PORT_PCR_MUX(1) | PORT_PCR_PE_MASK | PORT_PCR_PS_MASK;
    PORTA->PCR[SW2] = other_btn_cfg;
    PORTA->PCR[SW3] = other_btn_cfg;
    PORTA->PCR[SW4] = other_btn_cfg;
    PORTA->PCR[SW5] = other_btn_cfg;

    // 3. Set Port A pins to input
    PTA->PDDR &= ~(MASK(SW1) | MASK(SW2) | MASK(SW3) | MASK(SW4) | MASK(SW5));

    // 4. Enable Port A Interrupts in NVIC
    NVIC_SetPriority(PORTA_IRQn, 0); // Higher priority than PIT
    NVIC_ClearPendingIRQ(PORTA_IRQn);
    NVIC_EnableIRQ(PORTA_IRQn);
}
void PORTA_IRQHandler(void) {
    // 1. CLEAR FLAG IMMEDIATELY to prevent "ghost" pending interrupts
    uint32_t flags = PORTA->ISFR;
    PORTA->ISFR = flags; 

    if (flags & MASK(SW1)) {
        static uint32_t last_press_time = 0;
        uint32_t current_time = system_ms;
				/* Only act if 20ms has passed since the last valid press
         *(Since your PIT_Init is 0.001s, 20 counts = 20ms)
				 * 150ms is usually safe for human presses/releases
				*/
        if ((current_time - last_press_time) > 300) {
            program_start = !program_start;
            last_press_time = current_time;
        }
    }
}


void Init_LEDs(void){
	// Enable clock for poit C if not otherwise enabled
	//SIM->SCGC5 |= SIM_SCGC5_PORTC_MASK;
	// Set LED pins to GPIO
	PORTC->PCR[R_LED] &= ~PORT_PCR_MUX_MASK;
	PORTC->PCR[R_LED] |= PORT_PCR_MUX(1);
	PORTC->PCR[Y_LED] &= ~PORT_PCR_MUX_MASK;
	PORTC->PCR[Y_LED] |= PORT_PCR_MUX(1);
	PORTC->PCR[G_LED] &= ~PORT_PCR_MUX_MASK;
	PORTC->PCR[G_LED] |= PORT_PCR_MUX(1);
	// Set LED pins to outputs (1)
	PTC->PDDR |= MASK(R_LED)| MASK(Y_LED) | MASK(G_LED);
	// Initialize LEDs in off state by setting the port bits to zeros
	PTC->PCOR |= MASK(R_LED)| MASK(Y_LED) | MASK(G_LED);
	
}
void PIT_Init(float desired_period) {
		/*
		 *@param desired_period must be < 89.4 seconds
		*/
    // Enable clock to PIT module
    SIM->SCGC6 |= SIM_SCGC6_PIT_MASK;
    
    // Turn on PIT (MCR[MDIS] = 0)
    PIT->MCR &= ~PIT_MCR_MDIS_MASK;
    //Freeze timers when in debug mode
		PIT->MCR |= PIT_MCR_FRZ_MASK;
		// No chaining
		PIT->CHANNEL[0].TCTRL &= ~PIT_TCTRL_CHN_MASK;
	
    // Set load value for 1ms interrupt
    // Formula: (Bus Clock Frequency / Desired Frequency) - 1
    // (24,000,000 / 1000) - 1 = 47,999
		// Alt: (Sys Clock Frequency/2 * Desired Period) - 1
		uint32_t clk_cycles =  (uint32_t)(DEFAULT_SYSTEM_CLOCK * 0.5 * desired_period) - 1;
		// Initialize PIT0 to count down from argument 
		//PIT->CHANNEL[0].LDVAL = PIT_LDVAL_TSV(countsInPeriod);
    PIT->CHANNEL[0].LDVAL = clk_cycles;
    
    // Enable Interrupt and Start Timer (TIE and TEN)
    PIT->CHANNEL[0].TCTRL |= PIT_TCTRL_TIE_MASK | PIT_TCTRL_TEN_MASK;
    
    // Enable PIT IRQ in NVIC
    NVIC_ClearPendingIRQ(PIT_IRQn);
    NVIC_SetPriority(PIT_IRQn, 2);
    NVIC_EnableIRQ(PIT_IRQn);
}
void PIT_IRQHandler(void) {
    // Check if interrupt flag is set for Channel 0
    if (PIT->CHANNEL[0].TFLG & PIT_TFLG_TIF_MASK) {
        // Clear the flag by writing 1 to it
        PIT->CHANNEL[0].TFLG = PIT_TFLG_TIF_MASK;
        
        // Increment our counters
        system_ms++; // This is our "Wall Clock" for debouncing
        pit_count++; // This is our "Stopwatch" for the selected program
			
			// Visual TEST ONLY: Toggle the Green LED every interrupt
      // Use PTOR (Port Toggle Output Register) for a simple flip
      PTC->PTOR = MASK(G_LED);
    }
}

int get_bpm(uint32_t counts) {
	//Calculates the time period based on PIT cycles
    int bpm = 0;
    // 60,000 ms per minute. 
    // Assuming Freq_pit = 1000 Hz (1 ms per count)
    if (counts > 0) {
        bpm = 60000 / counts; 
    }
    if (bpm > 999) {
        bpm = 999; // Cap overflow
    }
    return bpm;
}
void displayString(char* str, int line) {
	/**
 * Displays a string on the specified LCD line.
 * @param str:  The string to display (max 8 chars)
 * @param line: 0 for the top line, 1 for the bottom line
 */
    // 1. Move cursor to the start of the requested line
    if (line == 0) {
        LCD_command(0x80); // Line 0 (t0p) address
    } else {
        LCD_command(0xC0); // Line 1 (bottom) address
    }

    // 2. Print up to 8 characters, or until the end of string
    int i = 0;
    while (str[i] != '\0' && i < 8) {
        LCD_send_data(str[i]);
        i++;
    }

    // 3. Optional: Fill remaining spaces with blanks to clear old data
    while (i < 8) {
        LCD_send_data(' '); 
        i++;
    }
}
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
